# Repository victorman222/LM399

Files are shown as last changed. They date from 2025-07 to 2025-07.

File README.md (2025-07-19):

LM399/ADR1399 reference

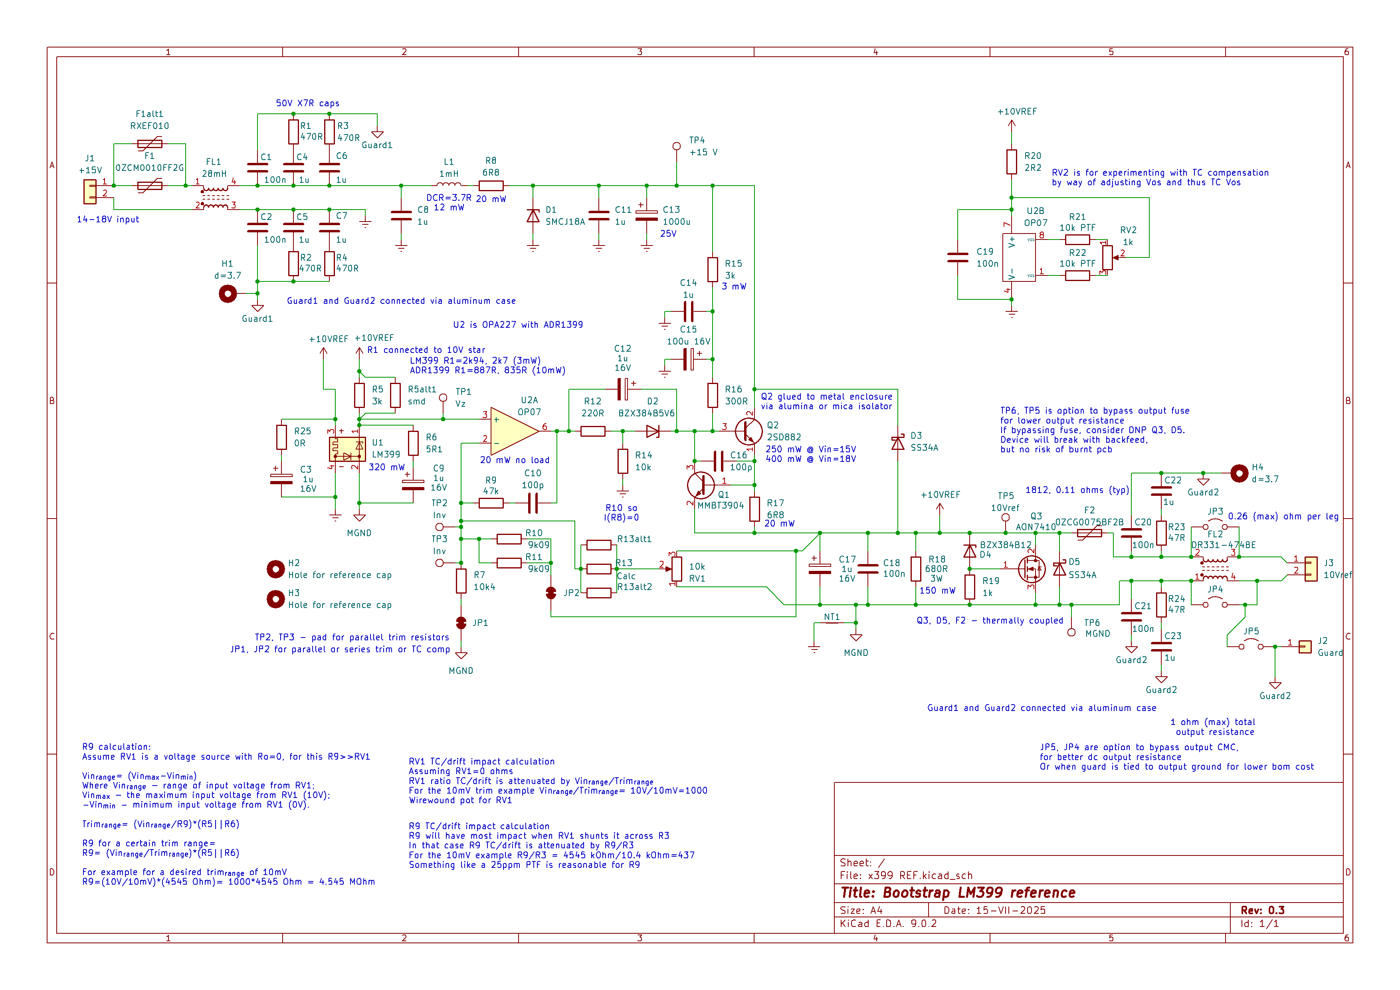
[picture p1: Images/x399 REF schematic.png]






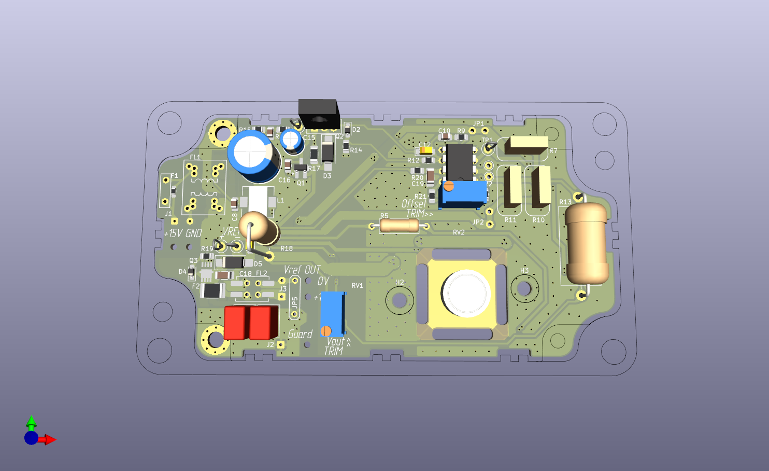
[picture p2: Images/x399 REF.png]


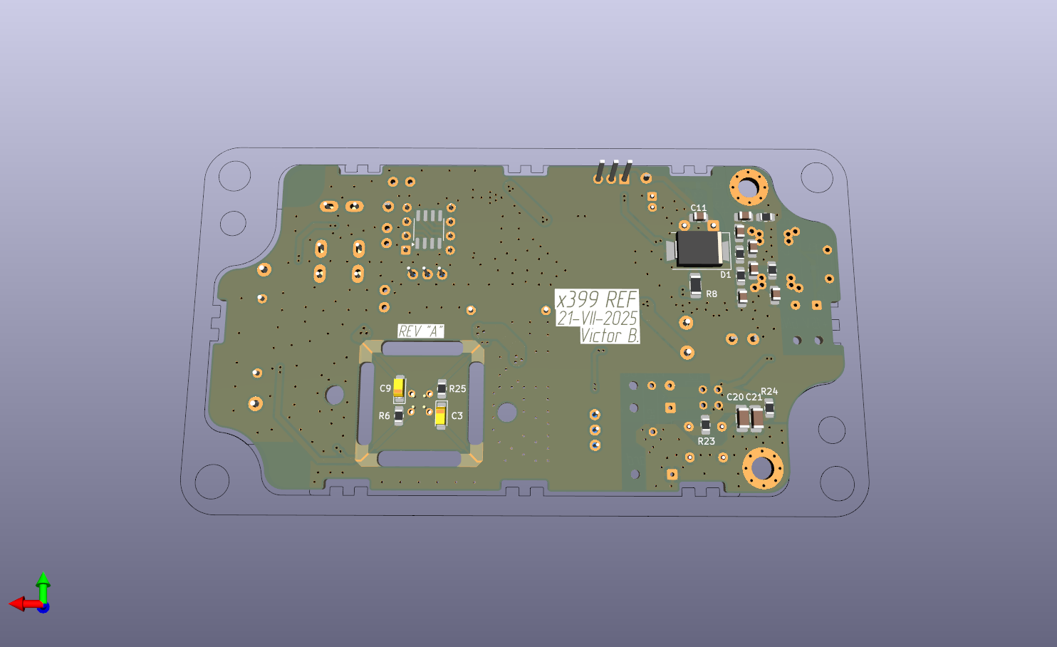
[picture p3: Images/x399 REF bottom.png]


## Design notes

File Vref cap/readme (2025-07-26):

3D models of cap to protect LM399 IC from air currents

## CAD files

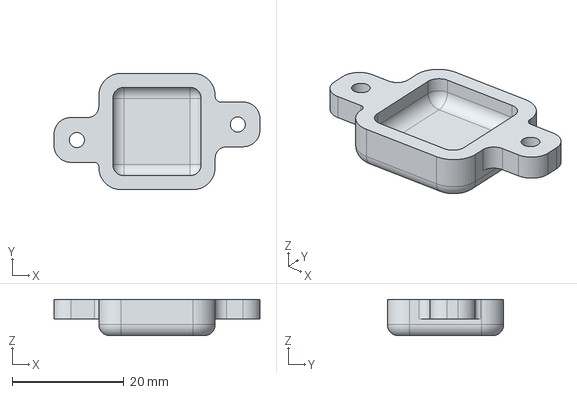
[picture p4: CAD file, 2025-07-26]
Vref cap/Bottom part.step
36.8 x 20.8 x 6.50 mm

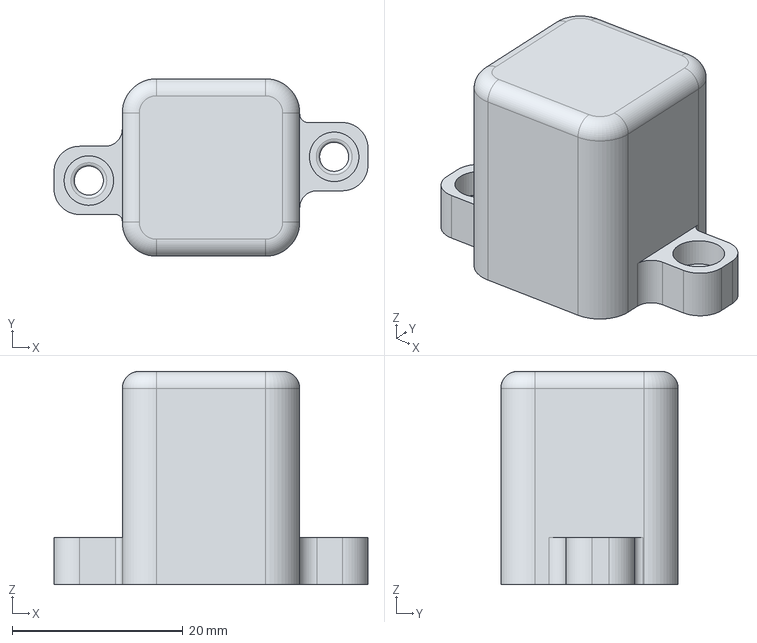
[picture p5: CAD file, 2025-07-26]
Vref cap/Top part.step
36.8 x 20.8 x 25.0 mm

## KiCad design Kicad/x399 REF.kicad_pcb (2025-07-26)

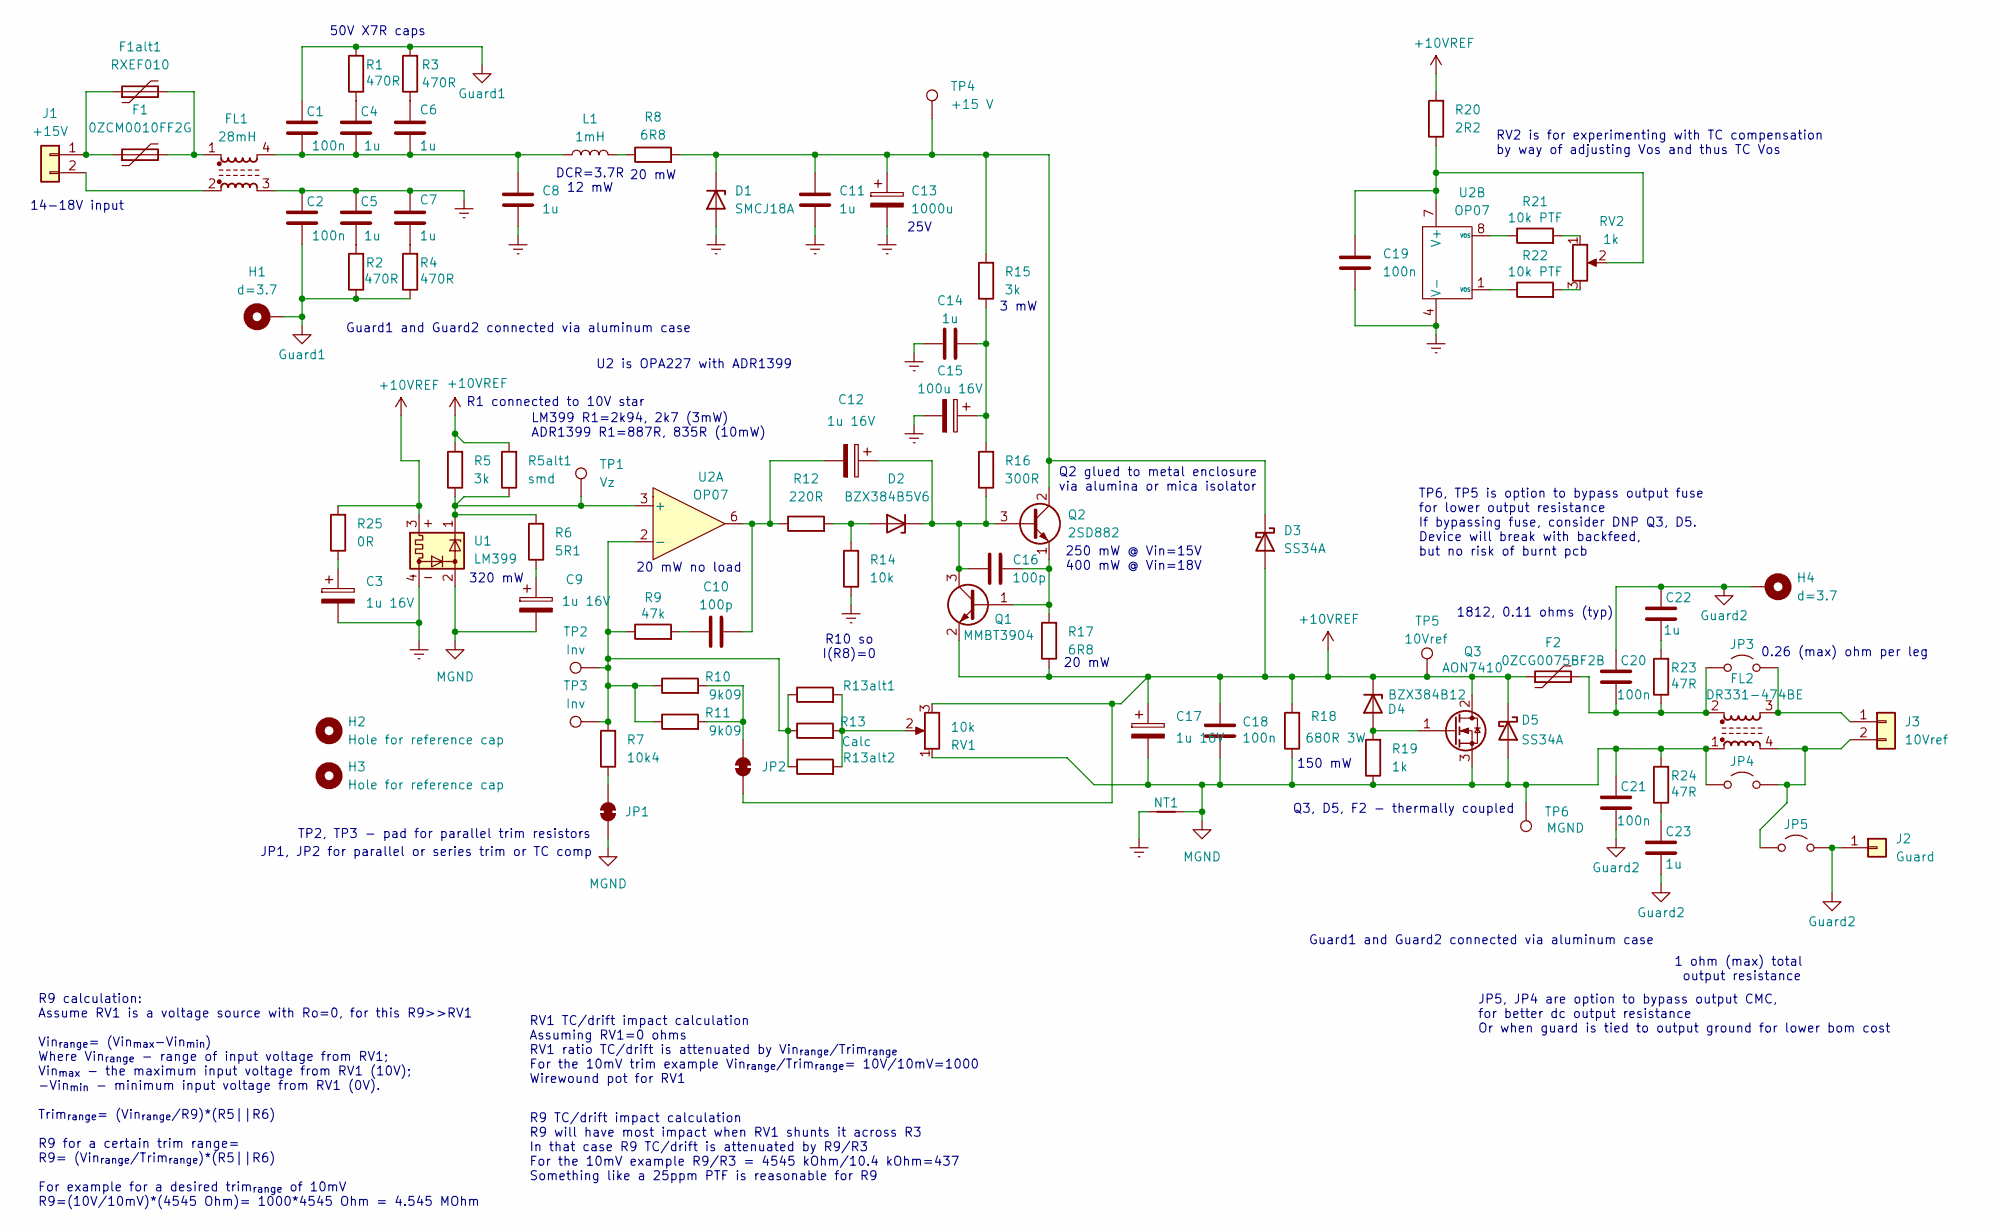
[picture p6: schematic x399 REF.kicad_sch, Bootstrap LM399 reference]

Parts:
C1, C2: 100n; C_0805_2012Metric_Pad1.18x1.45mm_HandSolder
C3, C9, C12, C17: 1u 16V; CP_EIA-3216-18_Kemet-A_HandSolder
C4, C5, C6, C7, C8, C11, C14: 1u; C_0805_2012Metric_Pad1.18x1.45mm_HandSolder
C10, C16: 100p; C_0805_2012Metric_Pad1.18x1.45mm_HandSolder
C13: 1000u; CP_Radial_D10.0mm_P5.00mm
C15: 100u 16V; CP_Radial_D5.0mm_P2.00mm
C18, C19, C20, C21: 100n; C_1206_3216Metric_Pad1.33x1.80mm_HandSolder
C22, C23: 1u; C_Rect_L7.2mm_W5mm_P5.00mm_FKS2_FKP2_MKS2_MKP2
D1: SMCJ18A; D_SMB-SMC_Universal_Handsoldering
D2: BZX384B5V6; D_SOD-323_HandSoldering
D3, D5: SS34A; D_SMA_Handsoldering
D4: BZX384B12; D_SOD-323_HandSoldering
F1: 0ZCM0010FF2G; R_0603_1608Metric_Pad0.98x0.95mm_HandSolder
F1alt1: RXEF010
F2: 0ZCG0075BF2B; R_1812_4532Metric_Pad1.30x3.40mm_HandSolder
FL1: 28mH; Universal line filter
FL2: DR331-474BE; L_CommonMode_Bourns_DR331_Handsolder
H1, H4: d=3.7; MountingHole_3.7mm_Pad_Via_6.7mm diameter
H2, H3: Hole for reference cap; MountingHole_3.2mm_M3
J1: +15V; SolderWire-0.1sqmm_1x02_P3.6mm_D0.4mm_OD1mm_Relief
J2: Guard; SolderWire-0.127sqmm_1x01_D0.48mm_OD1mm_Relief
J3: 10Vref; SolderWire-0.127sqmm_1x02_P3.7mm_D0.48mm_OD1mm_Relief
JP1, JP2: Joined holes D=1.8 Dh=0.9 P=3mm
JP3, JP4, JP5: TestPoint_2Pads_Pitch2.54mm_Drill0.8mm
L1: 1mH; L_7.3x7.3_H4.5_Handsoldering
NT1: NetTie-2_SMD_Pad2.0mm
Q1: MMBT3904; SOT-23_Handsoldering
Q2: 2SD882; TO-126-3_Vertical
Q3: AON7410; AO DFN3x3 EP GDS Handsoldering
R1, R2, R3, R4: 470R; R_0805_2012Metric_Pad1.20x1.40mm_HandSolder
R5: 3k; R_Axial_DIN0309_L9.0mm_D3.2mm_P12.70mm_Horizontal
R5alt1: smd; R_1206_3216Metric_Pad1.30x1.75mm_HandSolder
R6: 5R1; R_0805_2012Metric_Pad1.20x1.40mm_HandSolder
R7: 10k4; S5-61+vishay(150mil)+smd1206
R8, R17: 6R8; R_1206_3216Metric_Pad1.30x1.75mm_HandSolder
R9: 47k; R_0805_2012Metric_Pad1.20x1.40mm_HandSolder
R10, R11: 9k09; S5-61+vishay(150mil)+smd1206
R12: 220R; R_0805_2012Metric_Pad1.20x1.40mm_HandSolder
R13: Calc; R_Axial_DIN0918_L18.0mm_D9.0mm_P22.86mm_Horizontal
R13alt1: 0.6W tht; R_Axial_DIN0309_L9.0mm_D3.2mm_P12.70mm_Horizontal
R13alt2: 1206 smd; R_1206_3216Metric_Pad1.30x1.75mm_HandSolder
R14: 10k; R_0805_2012Metric_Pad1.20x1.40mm_HandSolder
R15: 3k; R_0805_2012Metric_Pad1.20x1.40mm_HandSolder
R16: 300R; R_0805_2012Metric_Pad1.20x1.40mm_HandSolder
R18: 680R 3W; R_Axial_DIN0617_L17.0mm_D6.0mm_P5.08mm_Vertical
R19: 1k; R_0805_2012Metric_Pad1.20x1.40mm_HandSolder
R20: 2R2; R_0805_2012Metric_Pad1.20x1.40mm_HandSolder
R21, R22: 10k PTF; R_0805_2012Metric_Pad1.20x1.40mm_HandSolder
R23, R24: 47R; R_0805_2012Metric_Pad1.20x1.40mm_HandSolder
R25: 0R; R_0805_2012Metric_Pad1.20x1.40mm_HandSolder
RV1: 10k; Potentiometer_Soviet_SP5-2VB
RV2: 1k; Potentiometer_Soviet_SP5-2VB
TP1: Vz; TestPoint_Loop_D2.50mm_Drill1.0mm
TP2, TP3: Inv; TestPoint_THTPad_D1.8mm_Drill0.9mm
TP4: +15 V; TestPoint_Loop_D2.50mm_Drill1.0mm
TP5: 10Vref; TestPoint_Loop_D2.50mm_Drill1.0mm
TP6: MGND; TestPoint_Loop_D2.50mm_Drill1.0mm
U1: LM399; Analog_TO-46-4_ThermalShield_balanced pins
U2: OP07; DIP-8_W7.62mm_W_soic_under

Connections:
+10VREF: C17.1, C18.1, D3.2 (A), D4.1 (K), D5.1 (K), F2.1, JP2.2 (B), Q1.2 (E), Q3.2 (D), R5.2, R5alt1.2, R17.1, R18.1, R20.2, R25.2, RV1.3, TP5.1, U1.3
Earth: C2.1, C3.2, C5.1, C7.1, C8.2, C11.2, C13.2, C14.1, C15.2, C19.2, D1.2 (A), FL1.3, NT1.1, R14.1, U1.4, U2.4 (V-)
Guard1: C1.1, C2.2, H1.1, R1.2, R2.1, R3.2, R4.1
Guard2: C20.1, C21.2, C22.1, C23.2, H4.1, J2.1, JP5.2 (B)
MGND: C9.2, C17.2, C18.2, C21.1, D5.2 (A), FL2.1, JP1.1 (A), JP4.1 (A), NT1.2, Q3.3 (S), R18.2, R19.1, R24.2, RV1.1, TP6.1, U1.2
unnamed: C1.2, C4.2, C6.2, C8.1, FL1.4, L1.1
unnamed: C3.1, R25.1
unnamed: C4.1, R1.1
unnamed: C5.2, R2.2
unnamed: C6.1, R3.1
unnamed: C7.2, R4.2
unnamed: C9.1, R6.1
unnamed: C10.1, R9.2
unnamed: C10.2, C12.2, R12.1, U2.6
unnamed: C14.2, C15.1, R15.1, R16.2
unnamed: C22.2, R23.2
unnamed: C23.1, R24.1
unnamed: C11.1, C13.1, D1.1 (K), D3.1 (K), Q2.2 (C), R8.2, R15.2, TP4.1
unnamed: D2.2 (A), R12.2, R14.2
unnamed: C12.1, C16.1, D2.1 (K), Q1.3 (C), Q2.3 (B), R16.1
unnamed: D4.2 (A), Q3.1 (G), R19.2
unnamed: F1.2, F1alt1.2, FL1.1
unnamed: F1.1, F1alt1.1, J1.1
unnamed: FL1.2, J1.2
unnamed: FL2.3, J3.1, JP3.2 (B)
unnamed: FL2.4, J3.2, JP4.2 (B), JP5.1 (A)
unnamed: JP1.2 (B), R7.1
unnamed: JP2.1 (A), R10.2, R11.2
unnamed: C20.2, F2.2, FL2.2, JP3.1 (A), R23.1
unnamed: L1.2, R8.1
unnamed: C16.2, Q1.1 (B), Q2.1 (E), R17.2
unnamed: R13.2, R13alt1.2, R13alt2.2, RV1.2
unnamed: R21.1, U2.8 (VOS)
unnamed: R21.2, RV2.1
unnamed: R22.1, U2.1 (VOS)
unnamed: R22.2, RV2.3
unnamed: R5.1, R5alt1.1, R6.2, TP1.1, U1.1, U2.3 (+)
unnamed: R7.2, R9.1, R10.1, R11.1, R13.1, R13alt1.1, R13alt2.1, TP2.1, TP3.1, U2.2 (-)
unnamed: C19.1, R20.1, RV2.2, U2.7 (V+)

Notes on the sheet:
20 mW
3 mW
Q3, D5, F2 - thermally coupled
Guard1 and Guard2 connected via aluminum case
LM399 R1=2k94, 2k7 (3mW) ADR1399 R1=887R, 835R (10mW)
TP2, TP3 - pad for parallel trim resistors
20 mW no load
1812, 0.11 ohms (typ)
50V X7R caps
TP6, TP5 is option to bypass output fuse for lower output resistance If bypassing fuse, consider DNP Q3, D5. Device will break with backfeed, but no risk of burnt pcb
250 mW @ Vin=15V 400 mW @ Vin=18V
R9 TC/drift impact calculation R9 will have most impact when RV1 shunts it across R3 In that case R9 TC/drift is attenuated by R9/R3 For the 10mV example R9/R3 = 4545 kOhm/10.4 kOhm=437 Something like a 25ppm PTF is reasonable for R9
1 ohm (max) total output resistance
R9 calculation: Assume RV1 is a voltage source with Ro=0, for this R9>>RV1 Vin_{range}= (Vin_{max}-Vin_{min}) Where Vin_{range} - range of input voltage from RV1; Vin_{max} - the maximum input voltage from RV1 (10V); -Vin_{min} - minimum input voltage from RV1 (0V). Trim_{range}= (Vin_{range}/R9)*(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
RV1 TC/drift impact calculation Assuming RV1=0 ohms RV1 ratio TC/drift is attenuated by Vin_{range}/Trim_{range} For the 10mV trim example Vin_{range}/Trim_{range}= 10V/10mV=1000 Wirewound pot for RV1
DCR=3.7R 12 mW
RV2 is for experimenting with TC compensation by way of adjusting Vos and thus TC Vos
25V
R10 so I(R8)=0
Q2 glued to metal enclosure via alumina or mica isolator
U2 is OPA227 with ADR1399
0.26 (max) ohm per leg
JP1, JP2 for parallel or series trim or TC comp
320 mW
150 mW
14-18V input
JP5, JP4 are option to bypass output CMC, for better dc output resistance Or when guard is tied to output ground for lower bom cost
R1 connected to 10V star

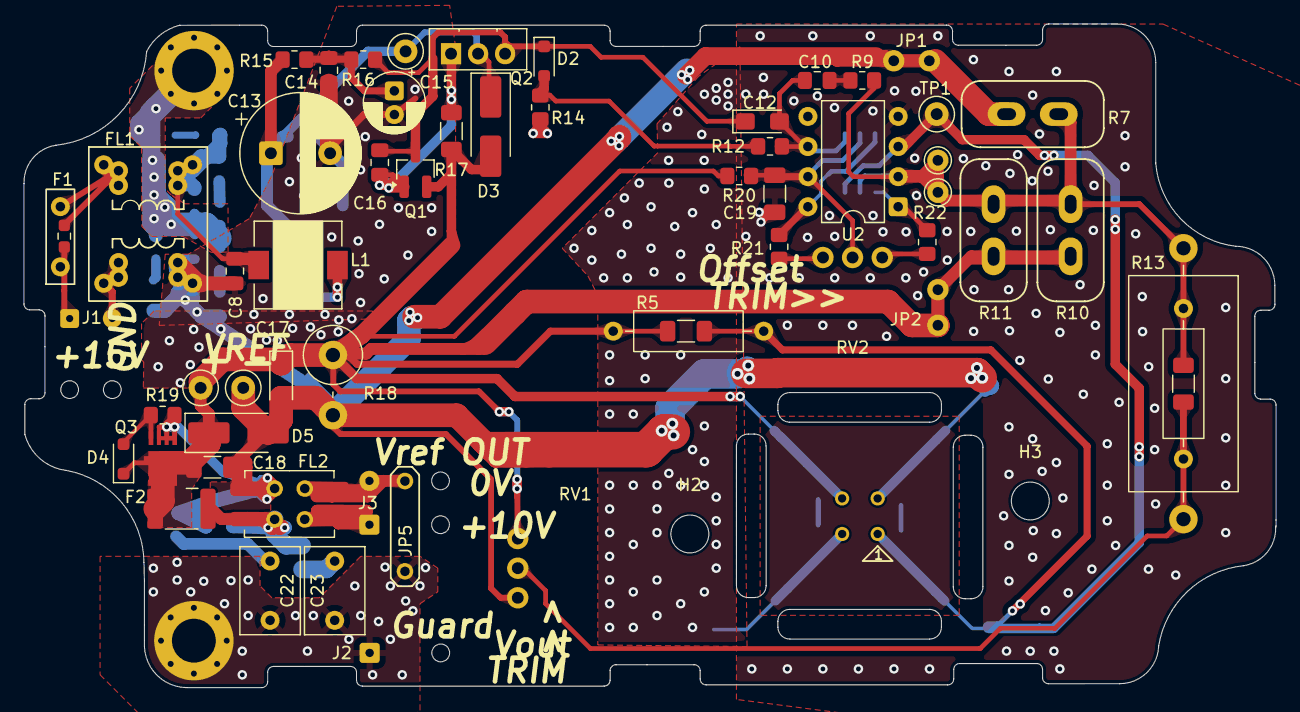
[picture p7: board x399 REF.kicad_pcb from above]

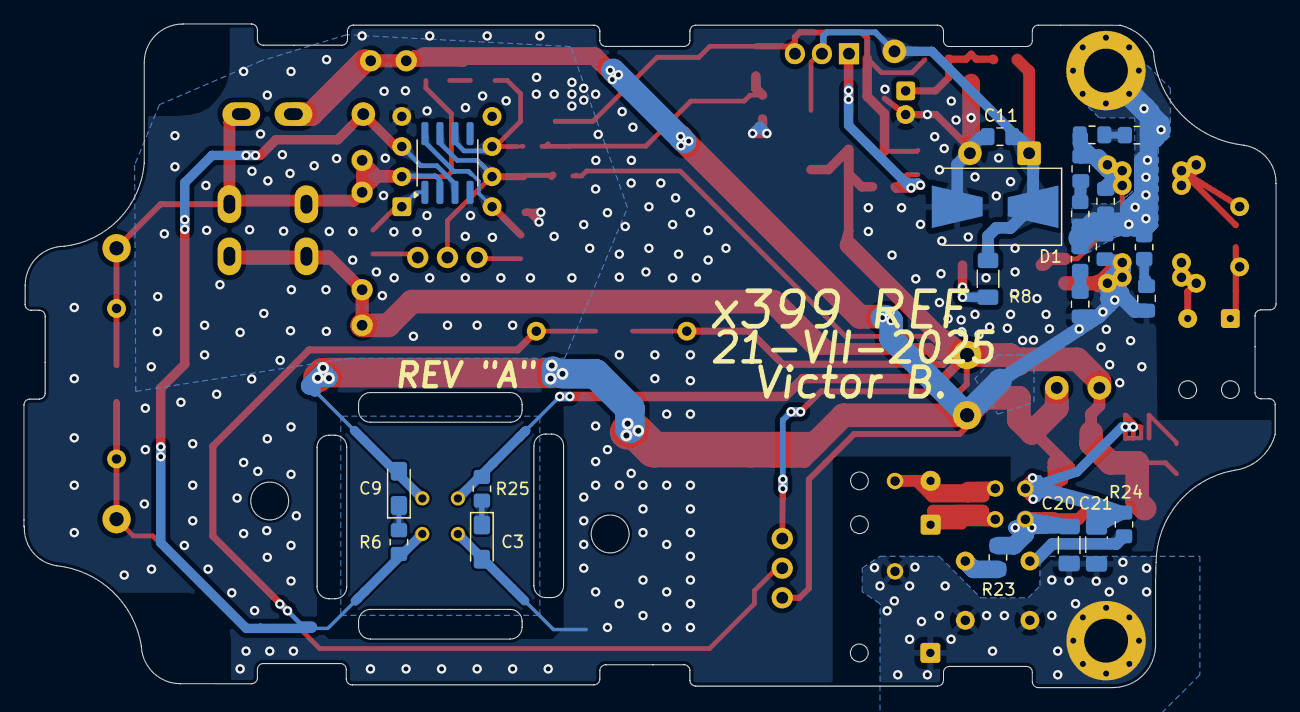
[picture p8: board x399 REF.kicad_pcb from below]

Board: 2 copper layers, 105.7 x 56.0 mm, 88 parts (22 on the bottom side), 39 nets.

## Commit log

2025-07-11 Board revision
    Rotated LM399 to have sensitive to TEMF pins (1,2) perpendicular to thermal gradient
    [x399 REF.kicad_pcb]
2025-07-11 Board revision
    Rotate transistor so it can be mounted to enclosure for heatsinking
    [x399 REF.kicad_pcb]
2025-07-11 Update images to latest board ver
2025-07-11 Update PCB drawings
2025-07-11 Replace DIP8-400mil wide footprint to standard 300mil
    [x399 REF.kicad_pcb, x399 REF.kicad_sch]
2025-07-21 Add files via upload
    Removed slots in middle of board, increased size of zener return trace and voltage divider traces
2025-07-25 Add files via upload
    Replaced guard 2 1u film capacitors for more accessible ones, improved thermal design on output
2025-07-25 Add files via upload
    Replaced guard2 1u film capacitors for more accessible ones, improved thermal design on output
    [x399 REF.kicad_pcb, x399 REF.kicad_sch]
